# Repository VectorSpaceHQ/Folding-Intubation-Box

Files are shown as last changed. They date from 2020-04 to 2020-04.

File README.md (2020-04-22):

# Folding-Intubation-Box
This is a folding intubation box designed by [Vector Space](https://vector-space.org) in Lynchburg, Virginia.

This design is a reinterpretation of the [EmoTech Airway box](https://www.youtube.com/watch?v=tWDG0Pa2EK4&feature=youtu.be). It is constructed from 1/4" clear polycarbonate and uses PVC hinges in order to avoid any metal fasteners or parts that could be lost.

 

## Materials
- 4'x4'x3/16" polycarbonate
- 6' of pinless PVC hinge (https://www.mcmaster.com/11195a43)
- WeldOn #40 adhesive

## Instructions
This box has 5 major parts,
1. Front
2. Top
3. 2 sides
4. 2 glove flanges
5. 3 hinges

These boxes can be made with or without the use of CNC tools. If made using manual methods, it is recommended to print the templates for help with routing the handles and drilling the hand holes. Polycarbonate can be cut using traditional woodworking tools. It is recommended that they be made and assembled in the following order. Use the folding_intubation_box.pdf for dimensions.

1. Cut 4'x4' sheet in half, leaving two 2'x4' sheets.
2. Cut one of these halves into 24"x26" (front) and 24"x20" (side) pieces.
3. Cut the other half into a 24"x28" (top) and 24"x20" (side) piece.
4. Cut the front piece down to 21.5"x26".
5. Cut the top piece down to 20"x28".
6. Use drill template to drill two 5" hand holes in front piece using hole saw
7. Use handle template to route handles into the side panels
8. Glue side panels to front panel using hinges
9. Glue top panel to front panel using hinge
10. Glue glove flanges to front panel

## Cleaning
It is recommended that Polycarbonate be cleaned with isopropyl alcohol.

---





---

Vector Space
https://vector-space.org

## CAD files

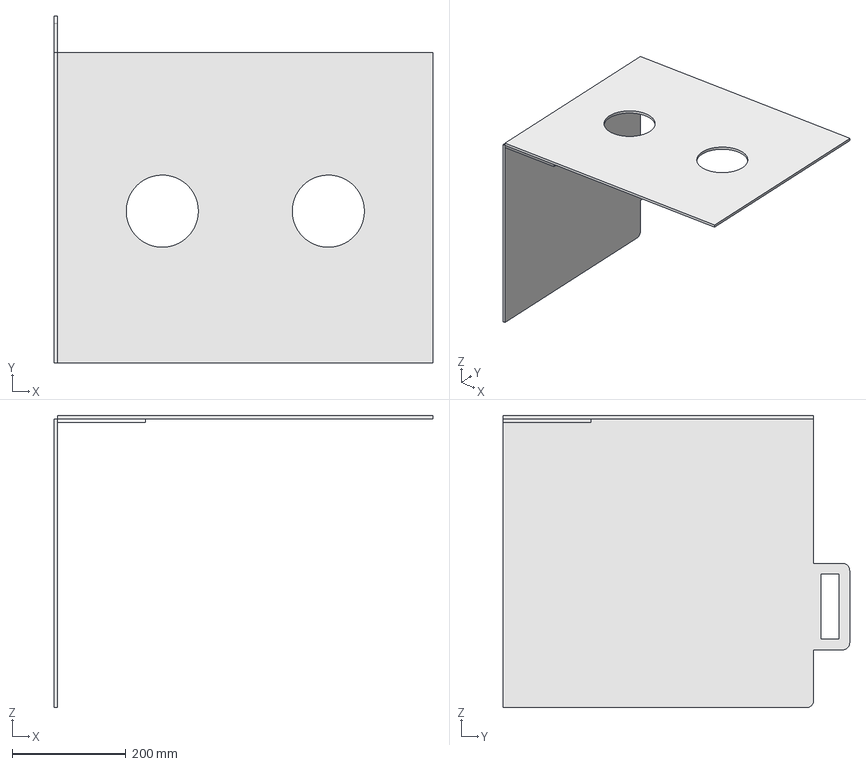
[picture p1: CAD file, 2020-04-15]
cad-cam/VS_folding_intubation_box.FCStd
666.8 x 609.6 x 514.4 mm
front
left
Stock

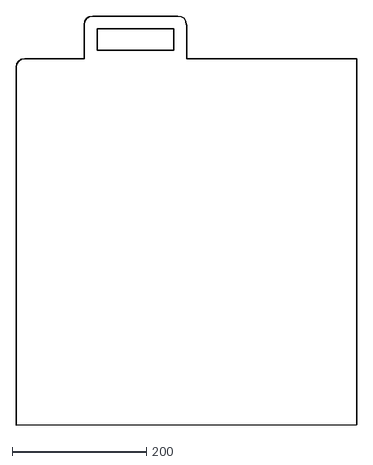
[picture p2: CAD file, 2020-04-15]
templates/side_panel.dxf
508.0 x 609.6

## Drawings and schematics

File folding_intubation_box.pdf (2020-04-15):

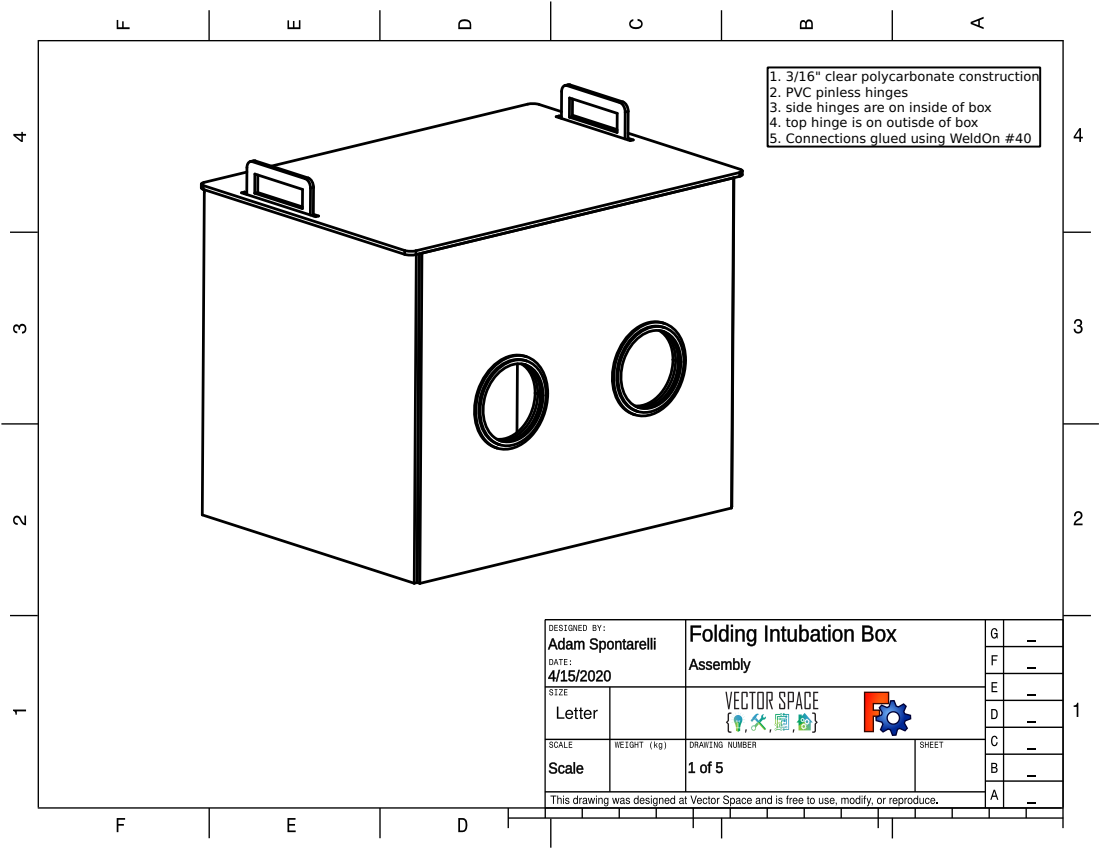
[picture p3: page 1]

1. 3/16" clear polycarbonate construction
2. PVC pinless hinges
3. side hinges are on inside of box
4. top hinge is on outisde of box
5. Connections glued using WeldOn #40

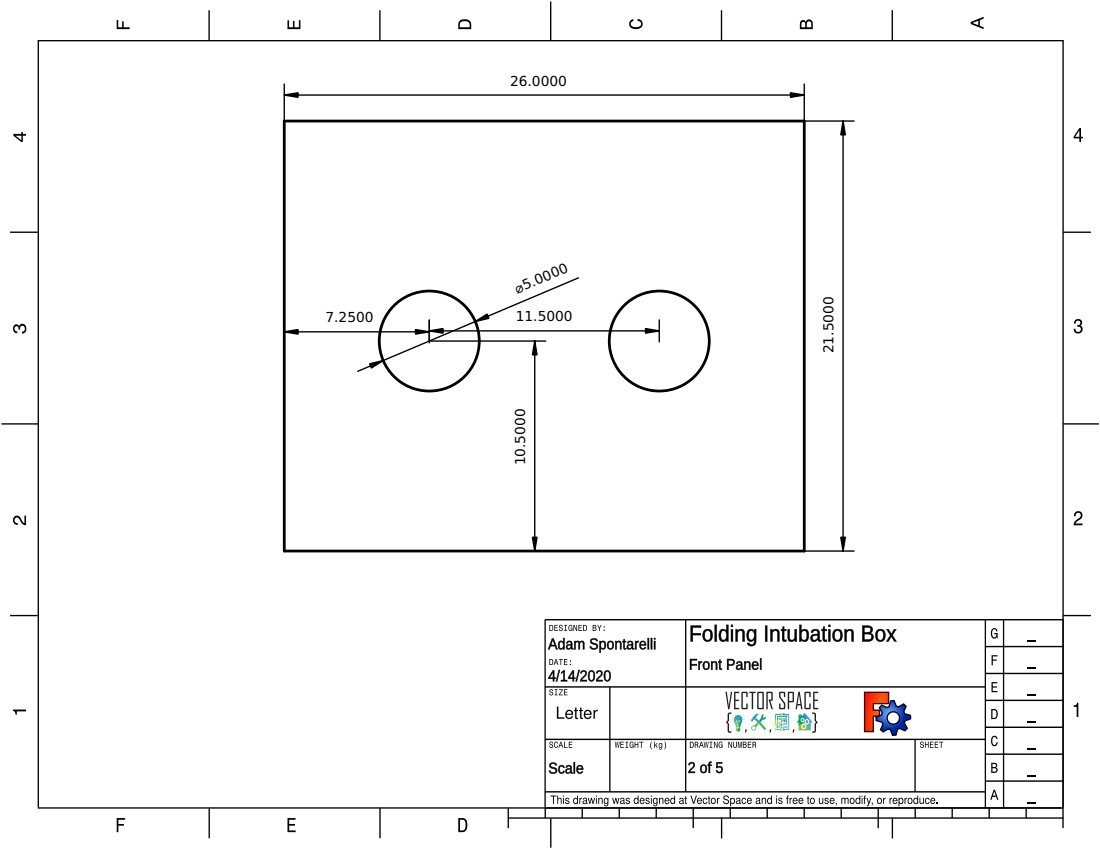
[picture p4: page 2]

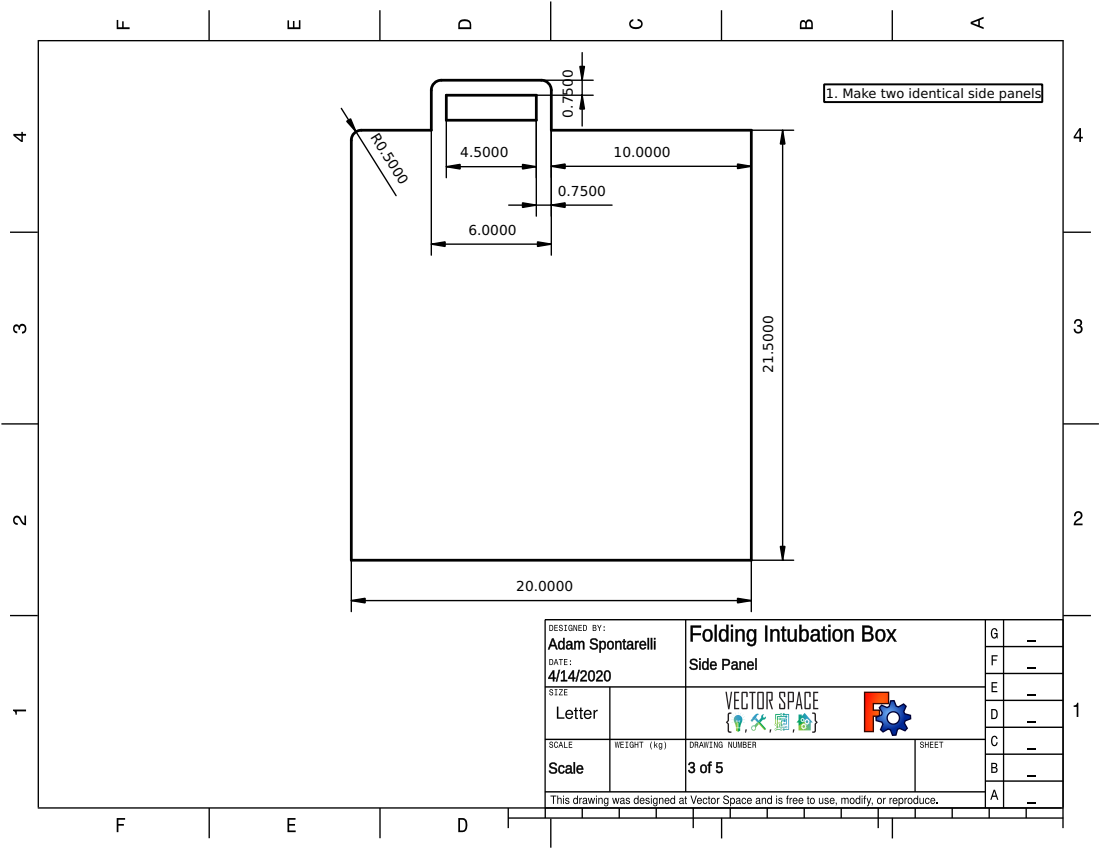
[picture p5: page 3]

1. Make two identical side panels

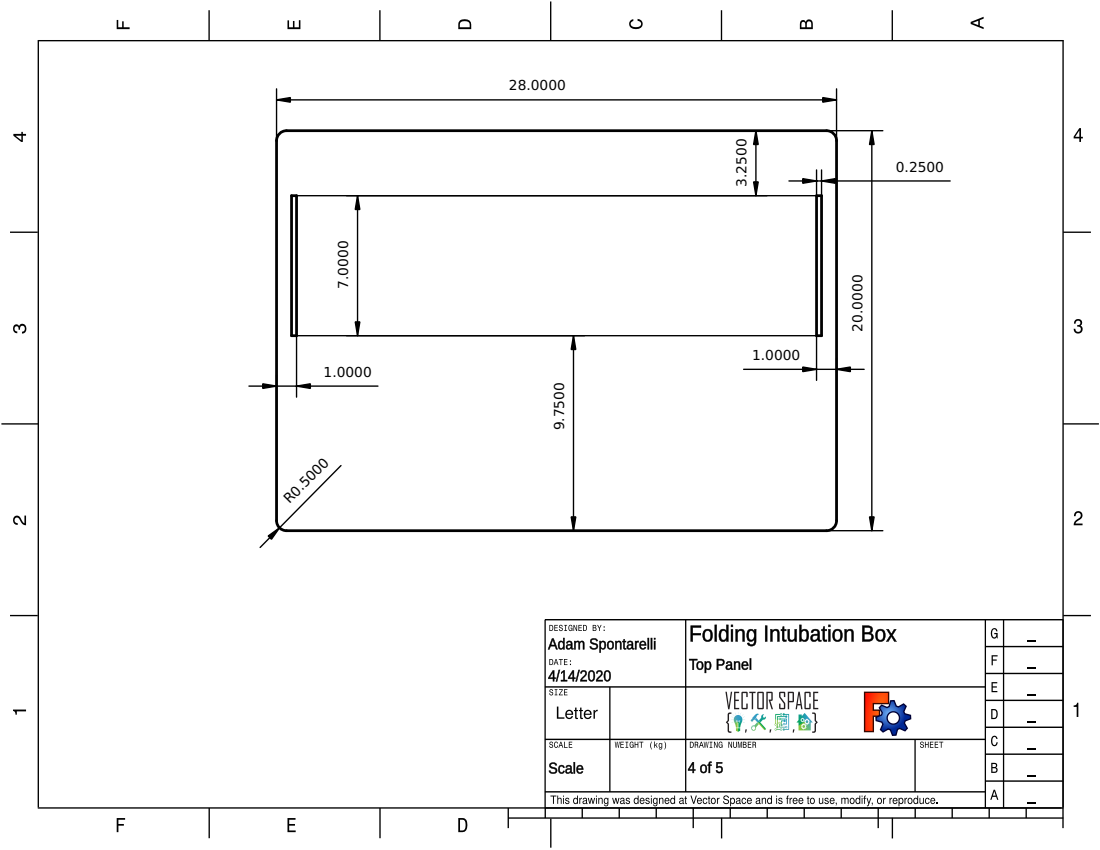
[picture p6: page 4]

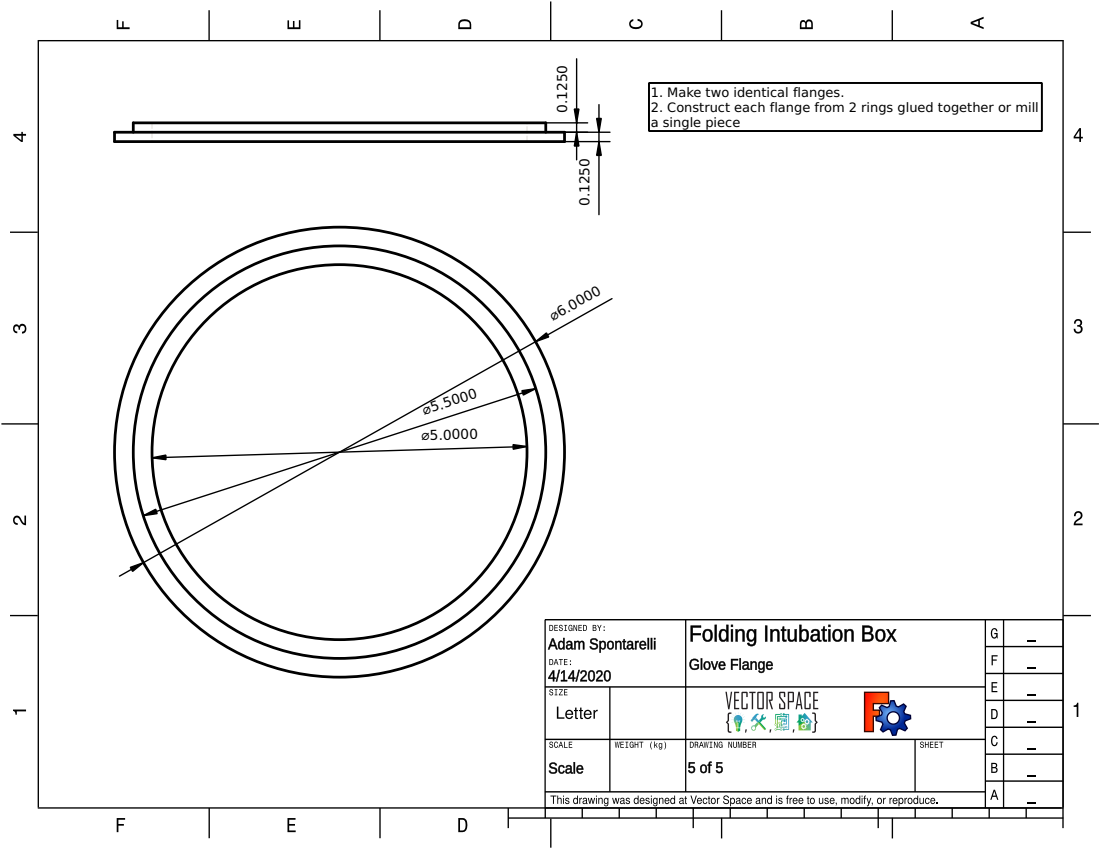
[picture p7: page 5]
a single piece

1. Make two identical flanges. 2. Construct each flange from 2 rings glued together or mill

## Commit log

2020-04-14 initial commit of FreeCAD file
    [VS_folding_intubation_box.FCStd]
2020-04-15 adding pdf drawings and templates
    [VS_folding_intubation_box.FCStd, side_panel.dxf]
